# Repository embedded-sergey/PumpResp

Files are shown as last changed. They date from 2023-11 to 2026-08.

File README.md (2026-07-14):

# PumpResp
PumpResp is an open‑hardware pump controller for intermittent‑flow aquatic respirometry. 

It is part of the FishResp project (more information at https://fishresp.org).

## Build Guide
The complete assembly, wiring, calibration, and safety instructions are provided in: `docs/PumpResp_Build_Guide.md`

This README intentionally avoids duplicating the Build Guide.

## Licensing
PumpResp uses a multi‑license structure:

- **Hardware designs:** CERN‑OHL‑S v2  
- **Software:** GPL‑3.0  
- **Documentation:** CC‑BY‑4.0  

Mixed‑content files (e.g., documentation containing schematics or code snippets) are governed by the license of each component.

See the **LICENSE** file for the human‑readable overview and the `LICENSES/` directory for full legal texts.

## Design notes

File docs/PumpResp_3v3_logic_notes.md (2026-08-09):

# PumpResp 3.3 V‑logic notes  
PumpResp can operate with 3.3 V‑logic Nano‑family boards (Nano 33 BLE, Nano 33 IoT, RP2040, Nano ESP32), which may provide additional functionality.

This topic is outside the scope of the main build guide. Several design and assembly adjustments are required, and the list below reflects unverified considerations only.

1. Replace the 5 V relay module with a relay module that is both 3.3 V‑logic compatible and powered from a 3–3.3 V supply.

2. The remaining PumpResp components (status LED, push button) operate correctly at 3.3 V logic level.
3.3 V I²C pins of the Arduino board (SDA and SCL)

3. If any connected device communicates over 5 V I²C, use a bidirectional logic‑level converter on the I²C lines (SDA and SCL). This protects the 3.3 V I²C pins of the Arduino board (SDA and SCL).

4. If PumpResp is connected over UART to the PyroScience FireSting logger, 3.3 V logic is actually preferable and aligns with the logger’s voltage levels.

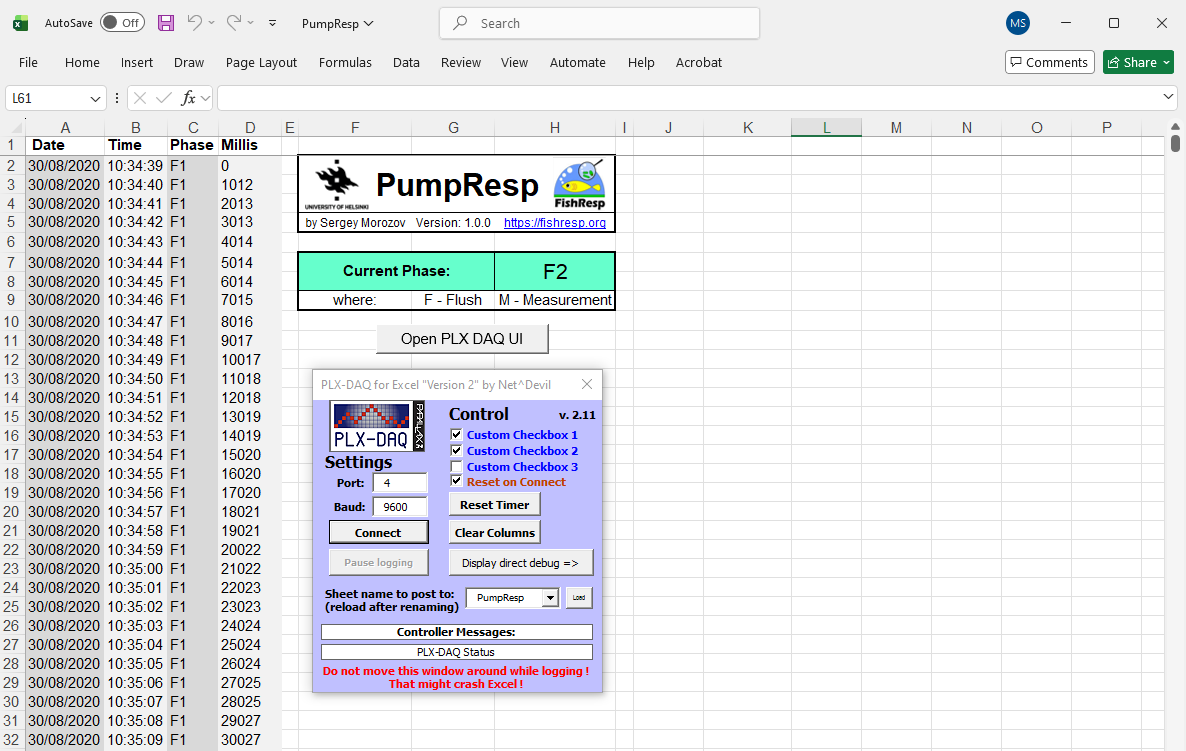
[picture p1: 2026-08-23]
docs/images/PumpResp_screenshot.png

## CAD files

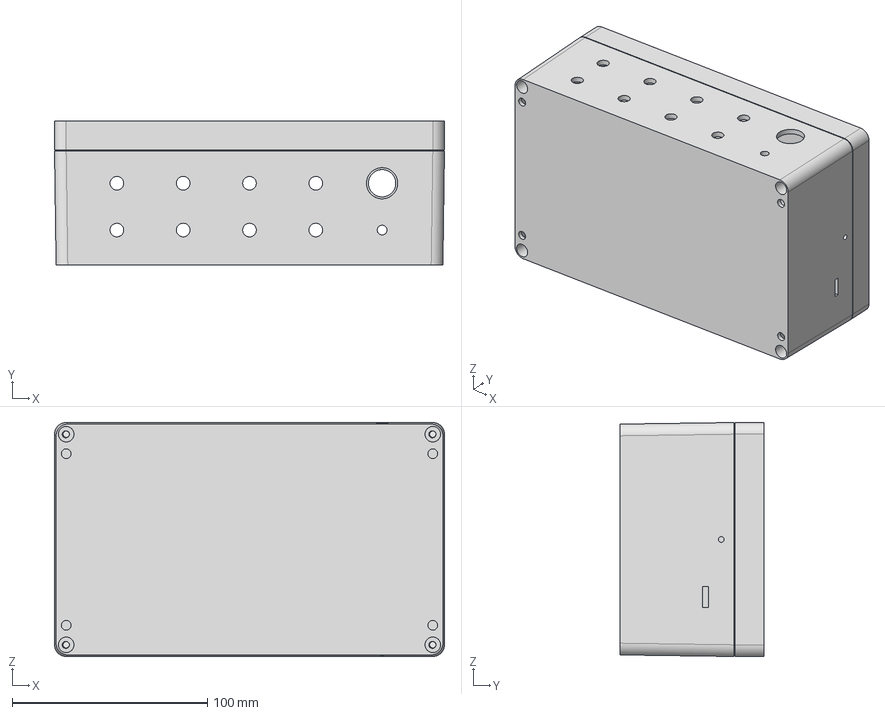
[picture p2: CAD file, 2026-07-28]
hardware/cad/PumpResp_enclosure_assembly.step
200.0 x 74.0 x 120.0 mm

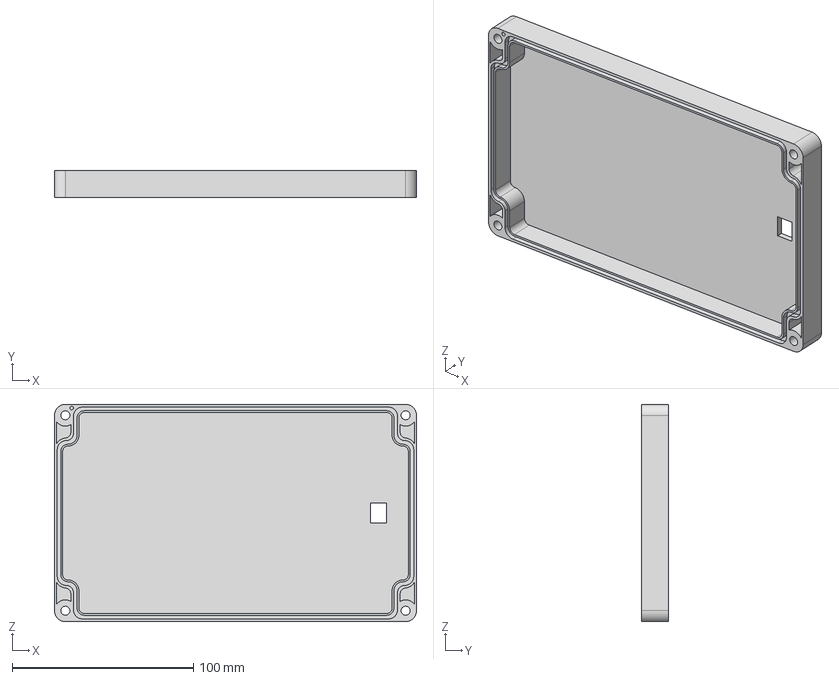
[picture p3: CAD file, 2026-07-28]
hardware/cad/PumpResp_enclosure_cover.step
200.0 x 15.0 x 120.0 mm

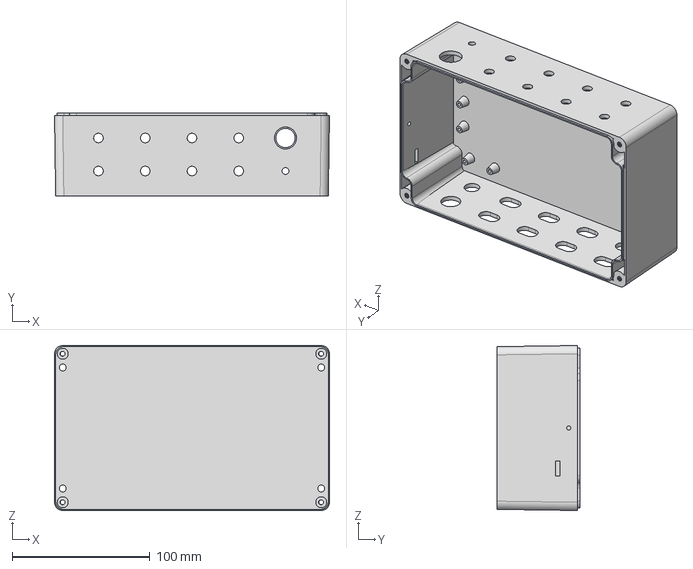
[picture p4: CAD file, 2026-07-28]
hardware/cad/PumpResp_enclosure_base.step
200.0 x 60.0 x 120.0 mm

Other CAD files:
hardware/stl/PumpResp_enclosure_base.stl
hardware/stl/PumpResp_enclosure_cover.stl

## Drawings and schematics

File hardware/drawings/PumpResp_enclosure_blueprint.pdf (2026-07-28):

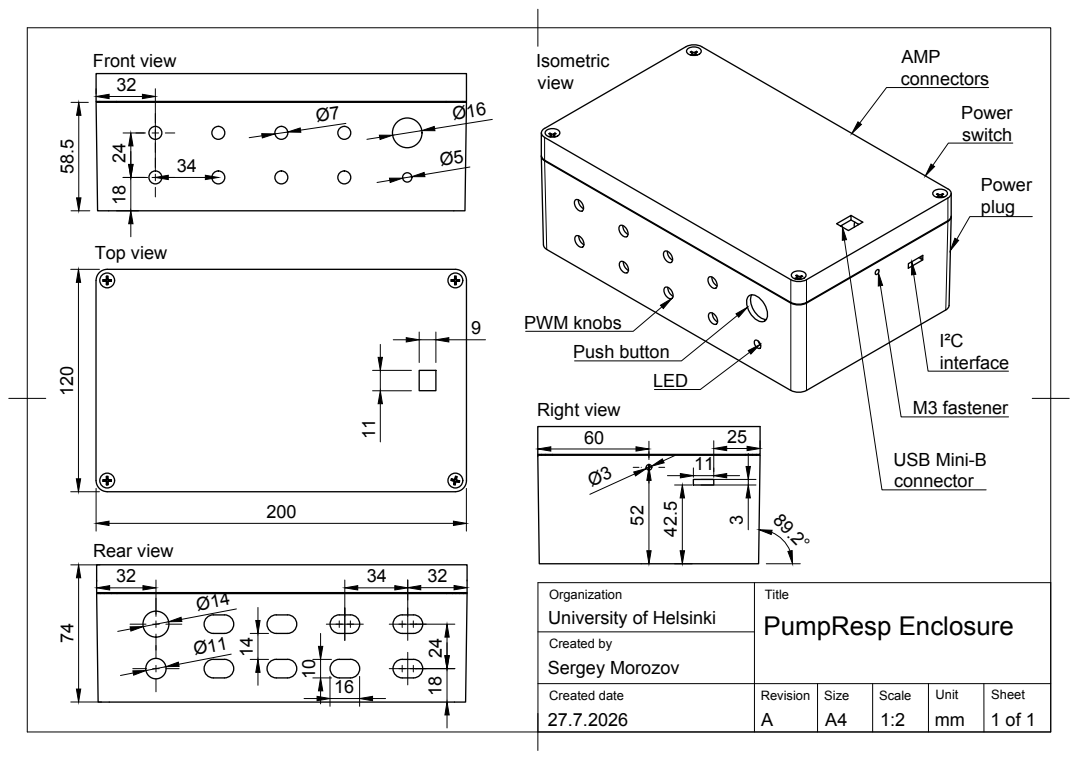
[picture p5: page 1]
Created date; Revision; Size; Scale; Created by; Sergey Morozov; PumpResp Enclosure; Push button; PWM knobs; M3 fastener; connectors 58.5; USB Mini-B; Front view; Top view; Rear view; Right view

University of Helsinki

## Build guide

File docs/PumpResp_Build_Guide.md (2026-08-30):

---
title: "PumpResp Build Guide"
author: "Sergey Morozov"
date: "30 August 2026"
revision: "0.7"
toc: true
toc-depth: 3
---

# PumpResp Build Guide
**Revision:** 0.7
**Author:** Sergey Morozov  
**Date:** 30 August 2026

<!-- begin-md-image -->
PumpResp Device
<!-- end-md-image -->

# Table of Contents

1. [Introduction](#1-introduction)
2. [Safety Notes](#2-safety-notes)  
   2.1 [Environmental Safety](#21-environmental-safety)  
   2.2 [Electrical Safety](#22-electrical-safety)  
   2.3 [Mechanical and Tool Safety](#23-mechanical-and-tool-safety)
3. [Bill of Materials](#3-bill-of-materials)
4. [Tools and Consumables](#4-tools-and-consumables)
5. [Assembly Instructions](#5-assembly-instructions)  
   5.1 [Preparing the enclosure](#51-preparing-the-enclosure)  
   5.2 [Installing power distribution components](#52-installing-power-distribution-components)  
   5.3 [Installing the control-side electronics](#53-installing-the-control-side-electronics)  
   5.4 [Adding the user interface components](#54-adding-the-user-interface-components)  
   5.5 [Enabling communication with other devices (optional)](#55-enabling-communication-with-other-devices-optional)  
   5.6 [Finalizing the enclosure](#56-finalizing-the-enclosure)
6. [Software Setup](#6-software-setup)   
   6.1 [Installing the Arduino IDE and uploading firmware](#61-installing-the-arduino-ide-and-uploading-firmware)   
   6.2 [Configuring the data‑logging software](#62-configuring-the-data‑logging-software)   
   6.3 [Establishing the serial connection and recording data](#63-establishing-the-serial-connection-and-recording-data)    
   6.4 [Exporting and managing recorded data](#65-exporting-and-managing-recorded-data)
7. [Functional Testing and Verification](#7-functional-testing-and-verification)
8. [Appendices](#8-appendices)

---

# 1. Introduction

PumpResp is an open‑source device for controlling pumps and recording pump‑phase data used in intermittent‑flow respirometry. It can operate up to eight 5–24 V DC pumps and transmit data to a computer over USB. The device can also communicate with external dissolved‑oxygen meters to enable threshold‑based pump activation in addition to simple time‑based control.

This guide explains how to assemble the hardware step by step. It covers preparing the enclosure, wiring the electronics, installing the user‑interface components, and loading the software. The document focuses strictly on construction and verification; experimental applications and biological context are described separately in the accompanying manuscript.

**User skill level.** The build guide is intended for students, technicians, and researchers with basic technical skills. No engineering background is required. Users should be comfortable with simple soldering and basic multimeter measurements (continuity and DC voltage).

**Assembly environment.** PumpResp can be assembled in any standard workspace equipped for basic electronics and mechanical tasks, including university or biological‑station workshops, applied‑sciences laboratories, or local FabLabs (a global directory is provided by the Fab Foundation). The enclosure can be purchased and modified or fabricated using a 3D printer.

**Estimated build time.** Assembly, software setup, and full functional verification typically require 2–4 days for a first‑time build depending on user skills. When assembling multiple identical units, the per‑device time decreases substantially as enclosure preparation and wiring become more routine.

## Versioning

This guide corresponds to PumpResp hardware, software, and documentation release **v1.0.0**.

Source files and updates are available in the public repository:  
<https://github.com/embedded-sergey/PumpResp>

## Licensing

- **Software:** GPL‑3.0  
- **Hardware designs:** CERN-OHL-S v2 
- **Documentation (including this guide):** CC‑BY‑4.0  

These licenses ensure open access, modifiability, and reproducibility across all components of the PumpResp platform. If this guide contains hardware diagrams or code snippets, those components are licensed under their respective hardware or software licenses.

# 2. Safety Notes

## 2.1 Environmental Safety

PumpResp is designed to be water-resistant, providing protection against accidental splashes and operation in high humidity environments. To reduce moisture accumulation in humid environment, place an absorbent pack inside the enclosure. PumpResp is not waterproof: if the device is submerged or dropped into the water, immediately power it off, disconnect the USB cable and do not resume operation until the enclosure and internal components have been thoroughly inspected and dried.

## 2.2 Electrical Safety

PumpResp operates at 5-24 VDC, which falls within the extra-low-voltage category recognized in electrical safety standards worldwide. Devices operating at ≤ 24 VDC are generally considered safe for personal, educational, and research use, and in most countries can be built and used without electrical certification, provided that a certified external power supply is used and no mains‑voltage wiring is modified. 

The power supply unit must include integrated overcurrent protection (fuse or electronic limit) and should be selected based on the total power requirements of the connected pumps. For example, if eight pumps each draw 0.3 A at 12 V, the total current is 2.4 A. In this case, a 12 V, 4 A power supply provides sufficient overhead for safe operation (i.e., operating below ~70% of the power supply unit's maximum rated output). The minimum recommended wire size for regular 5-12V is 24 AWG and 20 AWG for high‑current pump circuits.

During assembly and testing, follow basic electrical‑safety practices. Keep the device disconnected from any power source while you work. Check the polarity of every wire before connecting power, and avoid any contact between the positive and negative lines. Before turning the device on, inspect all solder joints, connectors, and insulation to make sure nothing is loose or exposed. Use a multimeter to check your wiring: confirm that each connection has continuity and make sure there are no accidental shorts. Switch the device on only when you’re sure all connections are correct.

## 2.3 Mechanical and Tool Safety

Use adhesive materials, mechanical and electrical tools listed in the section "Tools and Consumables” with care. If you are inexperienced with some of them, seek assistance from a trained technician. Wear personal protection equipment: protective glasses and fume mask, especially when soldering and use heat‑resistant mat to protect your workspace. During the assembly process run the tests referred in the assembly instructions to make the assembly process to be safe and verify the quality of PumpResp.

# 3. Bill of Materials

Price estimates for generic components use Amazon.com  as a reference, based on pricing available in August 2026. Amazon is chosen because it provides broad international availability, relatively stable pricing, and consistent product listings, which makes it a practical baseline for reproducible cost estimates. Because many components on Amazon are sold only in bulk packs, the bill of materials lists the price of the entire pack even when only one piece is needed, which inflates the apparent cost of a single device and results in unnecessary surplus. In practice, individual components can often be purchased at lower cost from suppliers that support small‑quantity or single‑unit purchasing, including local electronics stores, online marketplaces, and global engineering distributors such as Mouser or Digi‑Key. Prices for specialized sensors and measurement devices are taken directly from manufacturers’ websites when these items are not consistently available through the above distributors.

Prices listed in this BOM exclude VAT, customs duties, and delivery costs.

| Part Name | Manufacturer | Quantity | Unit Price (USD)¹ | Total Price (USD) | Notes |
|-----------|--------------|----------|--------------------|--------------------|-------|
| Industrial ABS enclosure, IP65, 200×120×75 mm | Generic | 1 pc | 10 | 10 | – |
| Male waterproof automotive connectors (Superseal 1.5‑style), 2‑pin | Generic | 1 set (10 male–female pairs) | 9 | 9 | Female connectors are also needed for pumps connected to PumpResp²|
| PWM motor speed controller, 1.8–12 V, 2 A | Generic | 8 pcs | 2 | 16 | 6–28 V PWM controllers can be used instead, but not with 5 V pumps |
| Red and black wires, 20 AWG | Generic | 3 m each | 7 | 7 | Use 16 AWG for high‑current pumps |
| Round rocker switch, mounting hole diameter 15 mm, 2-pin | Generic | 1 pc | 6 | 6 | Bulk pack (3–5 pcs) |
| DC power jack, steel, 5.5×2.1 mm | Generic | 1 pc | 7 | 7 | Bulk pack (3–5 pcs) |
| 1-channel relay, 5 V logic, 30 V, 10 A | Generic | 1 pc | 10 | 10 | Bulk pack (5–10 pcs). |
| Arduino Nano–compatible board (ATmega328P) with Mini-B USB cable and screw‑terminal adapter | Generic | 1 kit | 9 | 9 | The board can be replaced by the Arduino Nano rev.3 or 3.3 V-board from Nano family³ |
| M3 machine screw, 6 mm | Generic | 1 pc | 5 | 5 | Bulk pack (60–300 pcs) |
| Push button, mounting hole diameter 16 mm, 2-pin | Generic | 1 pc | 10 | 10 | Bulk pack (10 pcs) |
| LED, 5 mm | Generic | 1 pc | 6 | 6 | Bulk pack (50–200 pcs) |
| Resistor, 220 Ω, ¼ W | Generic | 1 pc | 6 | 6 | Bulk pack (20–200 pcs) |
| Female to male jumper wires, square jumpers, 10 cm | Generic | 1 kit | 5 | 5 | – |

**Grand total: 106 USD**²

*¹ Unit prices reflect the smallest purchasable quantity on Amazon.com. When only bulk packs are available, the listed price corresponds to the full pack even if a single piece is required.*

*² This BOM does not include motors or their cables.*

*³ This guide does not cover 3.3 V‑logic operation; refer to [PumpResp_3v3_logic_notes.md](PumpResp_3v3_logic_notes.md) for the necessary compatibility adjustments.*

# 4. Tools and Consumables
These items are not included in the BOM because they are general workshop supplies rather than project‑specific components, but they are still required for assembly. Most of the tools and consumables can be found in FabLabs, electronic/robotics clubs and Universities of Applied Sciences around the world.

Mechanical tools:
* utility cutter
* long-nose pliers
* wire cutters
* screwdriver
* drill with step drill bit
* rotary tool with 1 mm drill bit and cut‑off wheel

Electrical tools and materials:
* soldering iron
* solder wire
* flux
* heat-shrink tubing
* electrical tape

Adhesives:
* hot-glue gun
* hot-glue sticks
* superglue
* silicone tape

Measuring and marking tools:
* multimeter
* ruler
* pencil

Safety tools:
* protective glasses
* fume mask
* heat-resistant mat

# 5. Assembly Instructions
This section contains 36 assembly steps covering mechanical preparation, wiring, and installation of all power‑distribution and control components. Before beginning the assembly, note that several steps in Sections 5 and 6 have corresponding functional checks in Section 7. These checks can be performed immediately after completing each relevant assembly step or after the full assembly is finished. Performing the checks in parallel with assembly helps identify wiring mistakes early and reduces the risk of component damage.

## 5.1 Preparing the enclosure
PumpResp can be assembled using either a commercially available enclosure or the provided 3D‑printed enclosure. The printed version already includes all openings for the switch, power jack, and display, so drilling and cutting are not required (Steps 2–5). STL files are available in the SensResp repository.

**Step 1.** Unscrew the cover to open the enclosure.

**Step 2.** Mark the hole positions on the base and on the cover of the enclosure using a ruler and a pencil, following the dimensions shown in Figure 1.

Figure 1. Blueprint of the PumpResp enclosure  
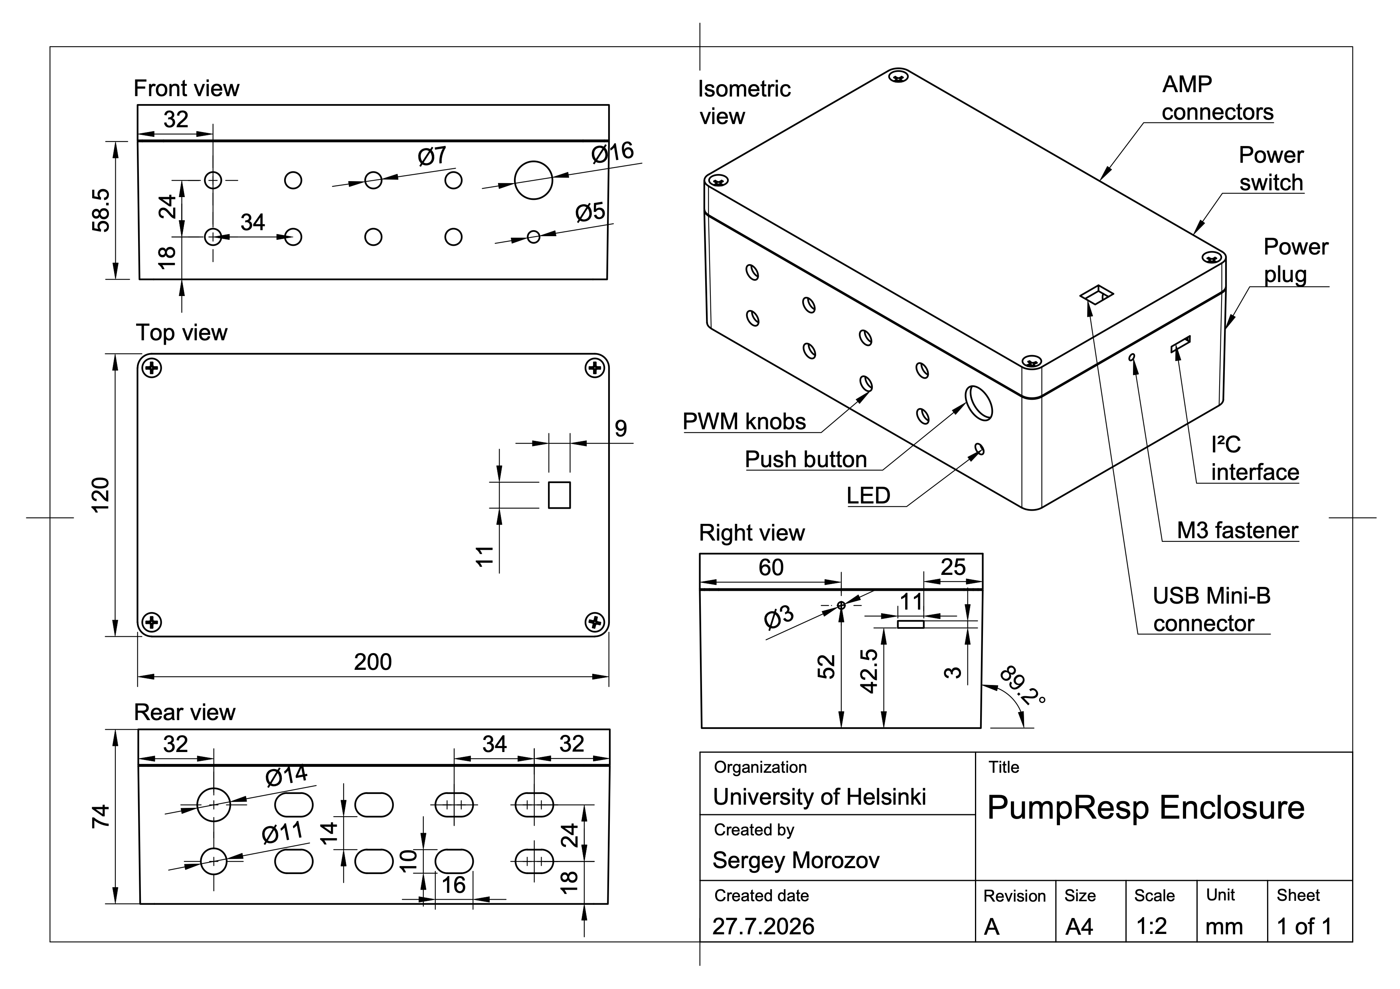
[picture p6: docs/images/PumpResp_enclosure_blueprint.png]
PumpResp enclosure blueprint


**Step 3.** If you use components with different form factors or an enclosure with different dimensions, adjust the blueprint. Alternatively, mark the hole positions directly on the enclosure.

**Step 4.** Drill the holes in the marked layout on the enclosure, then adjust the hole geometry using a utility cutter.

**Step 5.** For oval‑shaped holes on the rear panel, drill two overlapping holes and shape the opening with a cutter or a rotary tool, including the top recess.

**Step 6.** Remove the two protrusions on the bottom side of each body of a male waterproof connector using a utility cutter or a rotary tool with a cut‑off wheel.

**Step 7.** Assemble eight male waterproof connectors with 8 cm wires. Ensure that the red wire is inserted into port 1 of the connector and the black wire into port 2, respectively. Incorrect color order can lead to wiring errors.

**Step 8.** Insert the waterproof connectors into the oval‑shaped holes and secure them to the enclosure wall using a hot‑glue gun.

## 5.2 Installing power distribution components
**Step 9.** Mount the PWM controllers to the front panel of the enclosure.

**Step 10.** Connect the male waterproof connector wires to the Power (+) and Power (–) terminals of the corresponding PWM controller located in front of the connector as shown in Figure 2 (see [Check 1](#check-1-wiring-continuity-of-amp-plugs-and-pwm-modules)).

Figure 2. Wiring scheme of the PumpResp
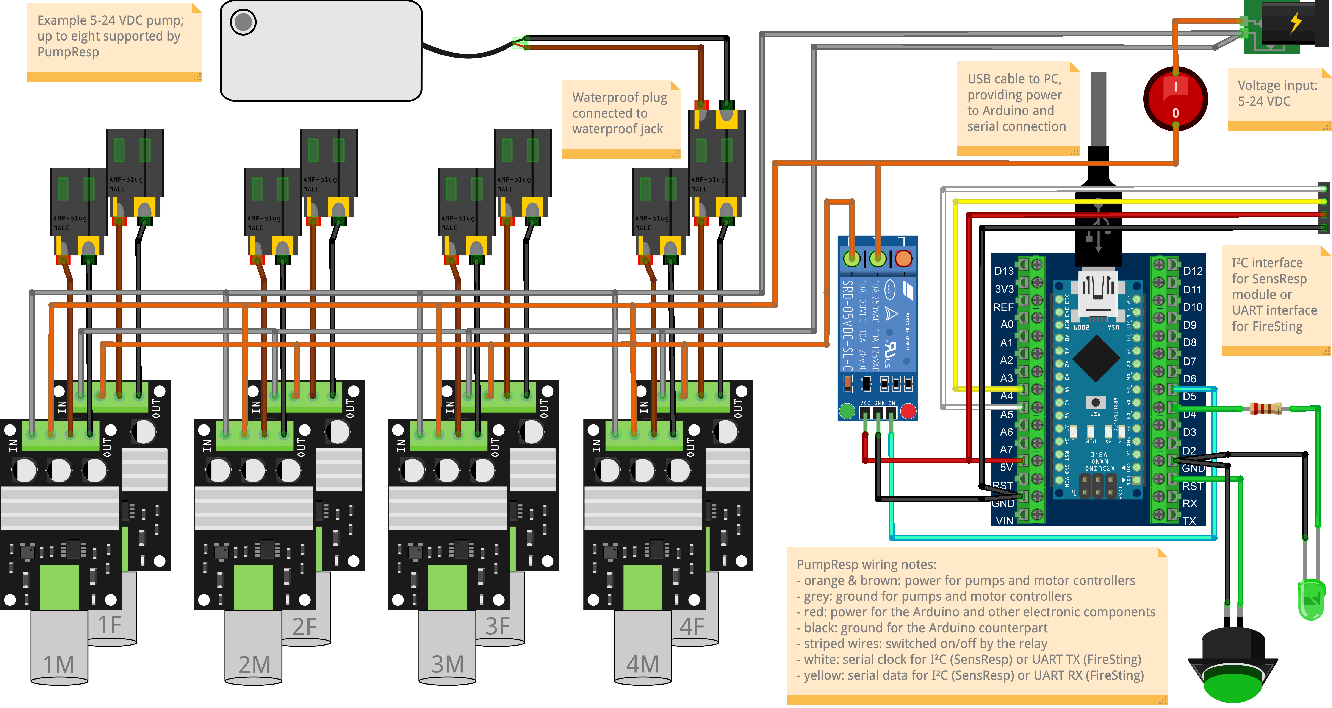
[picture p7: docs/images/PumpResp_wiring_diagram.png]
Wiring scheme of the PumpResp


**Step 11.** Assemble the two red and two black multi‑wire junctions by soldering the wire bundles as shown in Figure 3. Insulate all exposed solder joints with electrical tape, then secure the tape with a small drop of superglue to ensure no bare wires remain.

Figure 3. Assembly wires and multi‑wire junctions: 

**Step 12.** Connect the red wires to the Motor (+) and the black wires to the Motor (–) terminals of each PWM controller as illustrated in Figure 2.

**Step 13.** Mount the rocker power switch and the power connector to the rear panel of the enclosure.

**Step 14.** Solder the free ends of both black multi‑wire junctions to the ground pin of the power connector, then insulate the joint with heat‑shrink tubing.

**Step 15.** Solder the shortest red wire (shown in Figure 3) to the power pin of the power connector and the lower pin of the power switch.

**Step 16.** Solder the free end of the upper red multi‑wire junction and the remaining red wire to the upper pin of the power switch. This completes the high‑current power circuit (see [Check 2](#check-2-no-short-circuit-in-the-high-power-circuit) & [Check 3](#check-3-no-reverse-polarity-in-the-high-power-circuit)).

## 5.3 Installing the control-side electronics
**Step 17.** Place the relay board into the enclosure and connect the free end of the bottom red multi‑wire junction to the relay’s NO (Normally Open) terminal.

**Step 18.** Connect the remaining free end of the separate red wire, soldered to the power switch, to the relay’s Common (COM) terminal (see [Check 4](#check-4-powering-up-pwm-modules-and-dc-pumps)).

**Step 19.** Prepare the wire jumpers and remaining wires needed for the device assembly, as shown in Figure 3, using wire cutters.

**Step 20.** Mount the screw‑terminal adapter to a side wall of the enclosure using an M3 machine screw inserted into the hole, ensuring that the D12 and D13 labels are oriented at the top so that the Arduino Nano’s D12 pin aligns with the adapter’s D12 terminal. Install the Arduino Nano–compatible board (ATmega328P) into the screw‑terminal adapter.

**Step 21.** Connect the jumper wires to the relay board and secure the free wire ends in the screw‑terminal adapter as shown in Figure 2. For a cleaner layout and easier access to the Arduino and relay, route the red and black wires behind the terminal adapter as shown in Figure 4.

## 5.4 Adding the user interface components
**Step 22.** Solder the LED together with the 220 Ω resistor and the wires as shown in Figure 3. Ensure correct LED polarity (long leg is typically +).

**Step 23.** Mount the LED to the corresponding hole on the front panel of the enclosure using a hot-glue gun.

**Step 24.** Connect the LED’s wires to the corresponding pins of the screw‑terminal adapter as shown in Figure 2.

**Step 25.** Solder the green and black wires shown in Figure 3B to the push button.

**Step 26.** Install the push button on the front panel using its mounting nut.

**Step 27.** Connect the push button wires to the corresponding pins of the screw‑terminal adapter as shown in Figure 4 (see [Check 5](#check-5-no-wiring-faults-in-the-lowvoltage-control-circuit)).

Figure 4. Top view of the assembled device. 
TODO: ---

## 5.5 Enabling communication with other devices (optional)
**Step 28.** Make an additional rectangular hole on the side panel of the enclosure as shown in Figure 1. 

**Step 29.** Prepare four jumper wires using wire cutters. Glue the jumper heads together to form a four‑pin female connector as shown in Figure 4, so they remain aligned when inserted into the enclosure.

**Step 30.** Insert the connector into the rectangular opening and secure it to the enclosure wall using a hot‑glue gun (Figure 1, side view).

**Step 31.** Connect the free ends of the connector to the screw‑terminal adapter for communication through either I²C (for GalvaResp; use pins A4 and A5 as shown in Figure 2) or UART (for FireSting; use pins D2 and D3 instead, see Arduino Nano pinmap).

## 5.6 Finalizing the enclosure
**Step 32.** Insert the provided insulating material into the enclosure groove to prevent water contact between the environment and internal wiring.

**Step 33.** Fabricate a water-resistant layer that is attached to the USB cable connected to the Arduino Nano–compatible board (ATmega328P). This must fit the opening on the cover of the enclosure and can be made from silicone tape or another flexible waterproof material.

**Step 34.** Fabricate an additional water‑resistant lid to seal the opening during storage or when the USB cable is removed.

**Step 35.** Screw the cover securely to the base using the original mounting screws.

**Step 36.** Ensure the cover is seated evenly and that no wires are pinched when closing the enclosure.

# 6. Software Setup
This section describes how to program the Arduino Nano and configure the software required to record data from PumpResp. The workflow below reflects the configuration tested and validated for this build.

## 6.1 Configuring the data‑logging software
PumpResp was validated on Windows 10 using Microsoft Excel together with PLX-DAQ-2, an Excel-based serial data logger. This combination provides a straightforward installation process, stable serial communication, and direct data logging.

Install Microsoft Excel (version 2016 or newer) if it is not already available on your system. Download PLX‑DAQ‑2 version 2.11 from its original source: https://forum.arduino.cc/t/plx-daq-version-2-now-with-64-bit-support-and-further-new-features/420628. 

PumpResp includes a macro‑free Excel template (PumpResp_template.xlsx) containing recommended column names and formatting. This template is used together with PLX‑DAQ‑2 as described in Section 6.4.

Note that PLX‑DAQ‑2 is available only for Windows. Users working on macOS or Linux may employ alternative serial‑logging tools such as CoolTerm or Python with the PySerial library; however, these alternatives were not validated during development and are not covered in this guide.

## 6.2 Preparing the PumpResp Excel Environment
Since PLX‑DAQ‑2 cannot be redistributed after modification and does not include the PumpResp worksheet, users should set up the PumpResp environment locally. The setup is a simple, one‑time, five‑step process and requires no programming skills.

1. Unblock both PLX‑DAQ‑2.xlsm and PumpResp_template.xlsm because Windows blocks downloaded Excel macro files. Right‑click the .xlsm file, select 'Properties', tick 'Unblock' and press the 'Apply' button. In addition, "Enable Macros" / "Enable Content" in the pop-up message when Excel has been opened.

2. Copy the 'PumpResp' sheet into PLX‑DAQ‑2.xlsm. Open both PLX‑DAQ‑2.xlsm and PumpResp_template.xlsm, right‑click the PumpResp sheet tab, select "Move or Copy…" and select PLX‑DAQ‑2.xlsm, press OK. Close PumpResp_template.xlsm without saving.

3. Delete all sheets except PumpResp. Remove all other sheets in PLX‑DAQ‑2.xlsm so that only the PumpResp sheet remains.

4. Save the file PLX‑DAQ‑2.xlsm in Excel, close it and rename to PumpResp.xlsm.

Keep a backup copy of the assembled PumpResp.xlsm outside your experiment folders. If the file is lost or overwritten, it must be rebuilt using the steps in Section 6.2.

## 6.3 Installing the Arduino IDE and uploading firmware
PumpResp uses an Arduino Nano microcontroller (original or clone). To load the firmware:

1. Install Arduino IDE 2.0 or later from the official Arduino website.

2. Open the provided PumpResp.ino firmware file in the Arduino IDE.

3. Connect the Arduino Nano to your PC via USB.

4. In Tools → Board, select Arduino Nano.

5. In Tools → Processor, select ATmega328P (Old Bootloader) if you are using a common Nano clone.

6. In Tools → Port, select the COM port used by the Arduino Nano.

7. Install the SSD1306Ascii display library:
    - Open Sketch → Include Library → Manage Libraries…
    - Search for SSD1306Ascii
    - Click Install

8. Adjust the variable values in the USER INTERFACE section of the firmware according to your experimental design.

9. Click Upload (left‑arrow icon below the menu bar) to flash the firmware to the board. If the output panel shows no errors, you may close the Arduino IDE.

After uploading, the Arduino Nano will begin sending serial data over USB to PC (see [Check 6](#check-6-controlling-pumps-by-arduino-code)).

## 6.4 Establishing the serial connection and recording data
Open the PumpResp.xlsm file and click on "Open PLX DAQ UI" button there if it is not popped up automatically.

1. In the PLX‑DAQ‑2 control panel, select the serial port (COM number) corresponding to the connected Arduino Nano. 

2. Click Connect to open the serial port, initialize communication, and begin writing incoming data directly into the spreadsheet.

3. For improved performance and stability during long recordings, minimize the PLX‑DAQ‑2 control window while data collection is in progress. 

4. Note that editing the Excel sheet during the data collection might break the serial connection and Excel will be relaunched.

## 6.5 Exporting and managing recorded data
When data collection is complete, press Disconnect in the PLX‑DAQ‑2 control panel to close the serial connection. The recorded data remain in the spreadsheet and should be saved at this stage. Export the dataset either as a standard Excel workbook (.xlsx) or as a comma‑separated values file (.csv) for downstream analysis. If the Connect button is pressed again before exporting, the spreadsheet will be cleared and new data will overwrite the previous session. Always save or export the data before reconnecting to avoid accidental data loss (see [Check 7](#check-7-verifying-serial-communication-and-data-logging)).

After completing all assembly and software steps, perform the full‑system validation described in [Check 8](#check-8-full-system-test-with-submerged-pumps-and-currentdraw-safety).

For reproducibility, store the PumpResp.ino file used for the experiment together with the PumpResp.xlsm dataset or exported .csv file.

# 7. Functional Testing and Verification
This section provides a set of short, targeted functional checks to verify that PumpResp has been assembled correctly and operates safely before experimental use. Each check corresponds to an assembly or software step in Sections 5 and 6. Performing these checks reduces the risk of wiring errors, component damage, and hazardous operating conditions.

### Check 1: Wiring continuity of AMP plugs and PWM modules
Set the multimeter to audible continuity mode; in this mode, it emits a continuous beep when two points are electrically connected. Use the multimeter probes to check continuity between each wire of every AMP plug and the corresponding pin on its PWM module. Perform this for all eight plugs (two wires each). If there is no beep, the wire is not connected to the expected pin.

### Check 2: No short circuit in the high-power circuit
Using the same audible continuity mode, verify that none of the red (power) wires have continuity with the black (ground) wires. Test all accessible points of the multi-wire junction and other soldered connections you can reach with the probes. If the multimeter beeps, a short circuit is present and must be corrected before proceeding.

### Check 3: No reverse polarity in the high-power circuit
Ensure the power switch is in the Off (0) position. Power the device using the 5.5×2.1 mm jack from the power supply unit. Set the multimeter to DC voltage mode and measure the voltage between the power pin of the power connector and any ground point on the black multi‑wire junction. If the measured voltage is negative or significantly different from the rated output voltage of the power supply, the polarity is reversed or the wiring is incorrect and must be fixed before proceeding.

### Check 4: Powering up PWM modules and DC pumps
Ensure the device is powered and the power switch is in the On (1) position. Connect DC pumps with a maximum operating voltage below the rated output of the power supply unit to the AMP plugs. Rotate each PWM knob from its minimum (far left) to maximum (far right) position. Verify that the LED indicator brightens and the pump load increases. If not, replace the PWM module or the DC pump as appropriate.

### Check 5: No wiring faults in the low‑voltage control circuit
Before connecting the Arduino Nano to a USB port, set the multimeter to audible continuity mode and verify that no unintended connections exist between the screw‑terminal adapter pins used for the LED, push button, relay control, and optional communication lines (see Figure 2 and Appendix 1). Confirm that each signal pin (5V, RESET, D4, D5, D12, D13, and optionally A4/D2 and A5/D3) is isolated from ground and from all other signal pins. Any continuity between pins that are not directly wired together in the assembly steps indicates a wiring fault that must be corrected before powering the Arduino.

### Check 6: Controlling Pumps by Arduino code
Upload the Arduino sketch and verify that the pumps and LED respond correctly to the control signals defined in the user interface. Confirm that the lower pump line follows the programmed flow pattern, including the correct duration of the flush phase. Check that the LED indicates system state as intended: it blinks during the measurement phase (flushing pump off) and remains continuously on when the flushing pump is activated.

### Check 7: Verifying serial communication and data logging
After connecting PLX‑DAQ‑2 to the Arduino Nano, confirm that data are being transmitted and recorded correctly. Ensure that the spreadsheet begins populating with time‑stamped entries immediately after pressing Connect, and verify that data continue to append without interruption during the recording period. After pressing Disconnect, check that the recorded dataset remains intact and can be saved or exported without being overwritten.

### Check 8: Full system test with submerged pumps and current‑draw safety
Submerge the pumps in their experimental chambers and run the programmed flow cycle. Adjust pump speeds using the PWM module knobs and confirm that the resulting flow is stable and appropriate for the experiment. Turn the power switch to the Off (0) position. Set the multimeter to current‑measurement mode and place the probes across the two terminals of the power switch to measure the total current draw in series. Verify that the current remains well below the maximum output current of the power supply unit: ideally under 70% of its rated limit. During operation, ensure that the power supply unit becomes only moderately warm and never hot; excessive heating indicates overload or wiring faults that must be corrected before use.

Completing all eight checks ensures that PumpResp is fully functional, electrically safe, and ready for experimental use.

# 8. Appendices

Appendix 1: Schematics of PumpResp
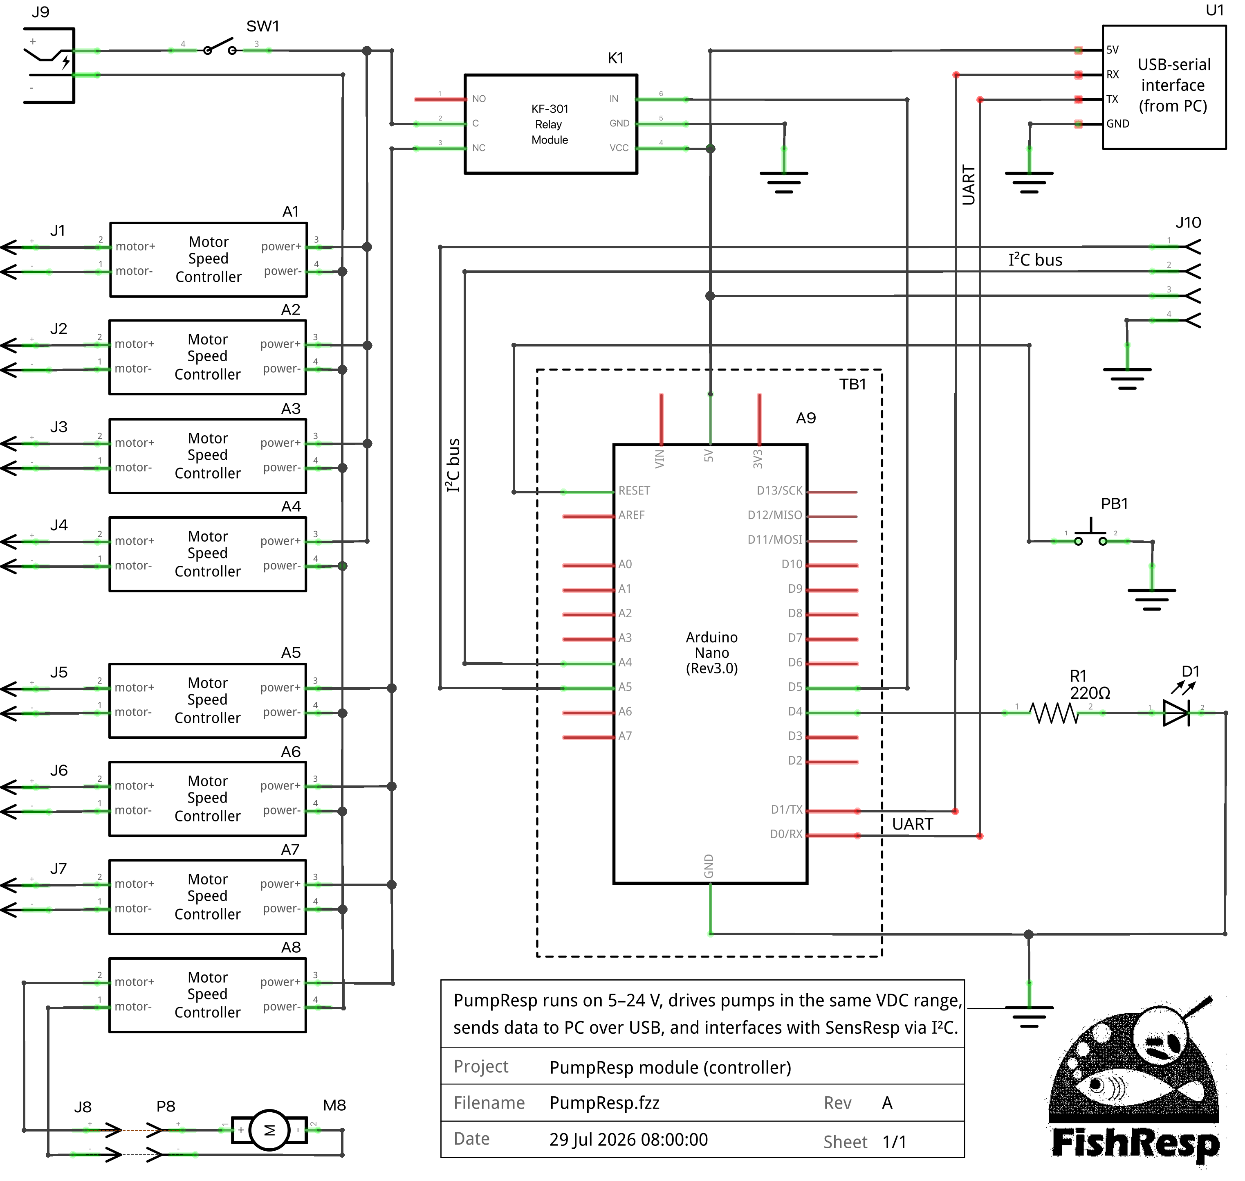
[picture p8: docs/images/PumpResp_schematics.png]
Schematics of PumpResp


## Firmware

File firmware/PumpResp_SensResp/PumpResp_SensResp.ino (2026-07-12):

////////////////////
// USER INTERFACE //
////////////////////

// Set the length of measurement and flush phases (in seconds)
int FLUSH = 5;       // LED is on
int MEASUREMENT = 15; // LED is blinking

/////////////////////////
// IMPLEMENTATION CODE //
/////////////////////////

// Include Arduino Wire library for I2C protocol
#include <Wire.h>
#define PumpResp_address 99 // define I2C address for PumpResp
#define PumpResp_size 5  // define the maximum size of 'Phase' string from PumpResp

int LED = 4;
int RELAY = 5;
int PERIOD = 1;
String phase, F, M, f = "F", m = "M";

void setup(){
   pinMode(RELAY, OUTPUT); 
   pinMode(LED, OUTPUT);
   
   Wire.begin(PumpResp_address);  // initialize I2C communications, slave/server mode
   Wire.onRequest(requestEvent);  // function to run when data requested from SensResp
   Wire.onReceive(receiveEvent);  // function to run when data received from SensResp
   
   Serial.begin(9600); // start the serial communication to the PC/SensResp
   Serial.println("CLEARRANGE,A,2,E,1000000"); // trick to get rid of AM-PM
   Serial.println((String) "LABEL, Date,Time,Phase,Millis"); // print the header of Excel sheet
}

void receiveEvent(){
  // Read while data received
  while (Wire.available() > 0) {
    byte x = Wire.read();
  }
}

void requestEvent(){
  // Setup byte variable in the correct size
  byte PumpResp_response[PumpResp_size];
  
  // Format the phase string as an array
  for (byte i=0;i<PumpResp_size;i++) {
    PumpResp_response[i] = (byte)phase.charAt(i);
  }
  
  // Send response back to SensResp
  Wire.write(PumpResp_response,sizeof(PumpResp_response));
}

void loop(){
   pinMode(RELAY, LOW); // set pin 3 OFF to turn off the relay,
                        // so pumps start working again.
                        
   for(int counter = 0; counter < FLUSH; counter++){       
         F = f + PERIOD;
         Serial.println((String) "DATA,DATE,TIME," + F +(",") + millis());
         digitalWrite(LED, HIGH);
         delay(1000); 
         phase = F;
      }

   pinMode(RELAY, HIGH); // set pin 3 ON to activate the relay,
                         // so pumps stop working
                         
   for(int counter = 0; counter < MEASUREMENT; counter++){      
         M = m + PERIOD;
         Serial.println((String) "DATA,DATE,TIME," + M +(",") + millis());
         digitalWrite(LED, HIGH);
         delay(200); 
         digitalWrite(LED, LOW);
         delay(800); 
         phase = M;
      }      
   
   PERIOD++;
}       

// Sources:
// 1. I2C mode instructions: https://dronebotworkshop.com/i2c-arduino-arduino/

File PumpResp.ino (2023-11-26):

// Version 1.1

////////////////////
// USER INTERFACE //
////////////////////

// Set the length of measurement and flush phases (in seconds)
int FLUSH = 5;        // LED is on, flushing pump is on
int MEASUREMENT = 15; // LED is blinking, flushing pump is off

// By default, the relay is active low. 
// Thus, if your relay is active high, reverse the variable values:
const byte RELAY_ON = LOW;
const byte RELAY_OFF = HIGH;

/////////////////////////
// IMPLEMENTATION CODE //
/////////////////////////

int LED = 5;
int RELAY = 3;
int PERIOD = 1;

void setup()
{
   pinMode(RELAY, OUTPUT);
   pinMode(LED, OUTPUT);
   Serial.begin(9600);
   Serial.println("CLEARRANGE,A,2,E,1000000"); // to get rid of AM-PM
   Serial.println((String) "LABEL, Date,Time,Phase,Millis");
}

void loop()
{
   digitalWrite(RELAY, RELAY_OFF); // set pin 3 OFF to turn off the relay,
                                  // so pumps start working again.

   for(int counter = 0; counter < FLUSH; counter++)
      {
         Serial.println((String) "DATA,DATE,TIME," + (String)"F"+PERIOD+(",") + millis());
         digitalWrite(LED, HIGH);
         delay(1000);
      }

   digitalWrite(RELAY, RELAY_ON); // set pin 3 ON to activate the relay,
                              // so pumps stop working

   for(int counter = 0; counter < MEASUREMENT; counter++)
      {
         Serial.println((String) "DATA,DATE,TIME," + (String)"M"+PERIOD+(",") + millis());
         digitalWrite(LED, HIGH);
         delay(200);
         digitalWrite(LED, LOW);
         delay(800);
      }

    PERIOD++;
}

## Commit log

2021-02-25 Added the file PumpResp_1.0.ino
2021-02-25 Added a new file PumpResp.xlsm, renamed PumpResp.ino, modified .gitignore
    [PumpResp.xlsm]
2021-02-25 Added version of the PumpResp.ino file at the first row.
2026-04-20 Write the core instructions for PumpResp
2026-05-10 Add verification section for device assembly
